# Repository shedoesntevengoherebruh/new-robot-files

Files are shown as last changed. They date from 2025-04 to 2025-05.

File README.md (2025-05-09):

This is the repository for the "BRONTE" (name subject to change) robotic chip-to-plate interface project.

Code and 3D model files are the joint work of Isabel B. Navarro and Gregory A. Datto.

>[!WARNING]
>
>_**This project (and its documentation) is still under development:**_ instructions are incomplete; the parts, object files, and code may change.

Thanks for stopping by the poster session!

P.S.— this is why it was really named BRONTE:

picture of BRONTE with scope

drawing of brontosaurus

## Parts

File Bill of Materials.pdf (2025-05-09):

## 1 Introduction

### 1.1 Bill of Materials

Designator | Manufacturer | Part # | Number | Cost/each | Total cost
| (Distributor)
Mechanical
Coupler | Uxcell | 1008917 | 1 (pack of 4) | $10.22 | $10.22
| (Harfington) | | (need 4)
Lead screw | McMaster-Carr | 99030A100 | 1 (3′
| | | length) | $46.42 | $46.42
Tapped shaft | McMaster-Carr | 6649K396 | 2 | $50.58 | $101.16
Ceramic-coated shaft | McMaster-Carr | 1031K72 | 2 | $16.52 | $33.04
3/8′′ linear bearing | AMPEC | SW06UU | 4 | $9.51 | $38.04
| (Bearings Direct)
3/8′′ ball bearing | AMPEC | R6-ZZ | 2 | $3.10 | $6.20
| (Bearings Direct)
1/4′′ shaft | McMaster-Carr | 1031K61 | 4 | $10.28 | $41.12
1/4′′ linear bearing | PBC Linear | IP04G | 4 | $17.04 | $68.16
M3 screw | McMaster-Carr | 92005A124 | 1 (pack of 100) | $5.79 | $5.79
| | | (need 16)
8-32 screw | McMaster-Carr | 91500A197 | 1(pack of 50) | $7.18 | $7.18
| | | (need 4)
Filament | ** | ** | **kgs | ≈ $20 | **
1/4′′ acrylic | AZM Displays | B07H9NQP8G | 1 (24′′x12′′) | $22.99 | $22.99
| (Amazon)
1/8′′ acrylic | McMaster-Carr | 8560K275 | 1 | $6.95 | $6.95
Electronics
Motor driver | Pololu | 2981 | 4 | $6.15 | $24.60
| (Digikey)
Permaproto boards* | Adafruit | 591 | 1 pack | $34.95 | $34.95
| (Microcenter)
NEMA-17 Motor with encoder | Stepper Online | 17HS15-1504-ME1K | 4 | $18.18 | $72.72
ESP32-s2 | Espressif | DevKitM-1-N4R2 | 1 | $8.00 | $8.00
| (Amazon)
Barrel jack adapter | Philmore | 48-1297 | 1 | $3.82 | $3.82
| (Microcenter)
Power supply | Alitove | ** | 1 | $37.99 | $37.99
| (Amazon)
Solder | ** | ** | ** | 1 | **
Pressure and Interface
Aluminum holder | ProtoLabs | N/A | N/A | ≈ $250 | ≈ $250
Headless Nut | IDEX | P-283 | 24 | $4.10 | $98.40
Ferrule | IDEX | P-200X | 1 *(pack of 10)* | $17.11 | $17.11
| | | (Need 6)
Luer Adapter | IDEX | P-625 | 8 | $5.21 | $41.68
Needle (Low Dead Space) | TSK | LDS-30009I | 1 (pack of 100) | $89.95 | $89.95
| (Air-Tite Products) | (TSK3009LDS) | (need 6)
Union | IDEX | *P-603 (white Delrin)* | 6 | $3.94 | $23.64
2-Port Kit | Elveflow | LVF-KPT-S-2 | 6 | $156.80 | $940.80
| (Darwin Microfluidics)
Pressure Regulator | Alicat Scientific | PCD-30PSIG-D-PCV30 | 6 | ≈$500 | ≈$3,000
| (eBay) | | | (Used)
DIN Jack | L-com | MD88FJF | 6 | $20.99 | $125.94

1

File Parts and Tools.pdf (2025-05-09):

# Methods Parts

## Tools

## Bill of Materials

See Bill of Materials PDF file.

## 3D printed pieces

This will be a table of the 3D printed parts, ideally with a picture or at least, color-coding of each one. I think the weight and time (when prepared as we did it), the number, the color (by our system), will be useful for people, along with the .stl or .obj filenames of each part, will be useful to include in the table.

Hammer/mallet (ideally, to help press-fit) 3D printer (with bed size at least X"xX"xX") set of small files
Allen key (Size X)
Phillips head screwdriver
Soldering station (with solder and fume extractor) hack saw (fresh blade ideal for cutting lead screw, etc.)

Tray (teal)
Carriage 1 (Yellow)
Carriage 1 endcaps (Yellow, 2×)
Carriage 2 (Magenta)
Carriage 2 endcap A and B (Magenta. Endcap A has the motor standoff.) "Big H" (white, 2×)
Lead screw nuts (black, 4×)

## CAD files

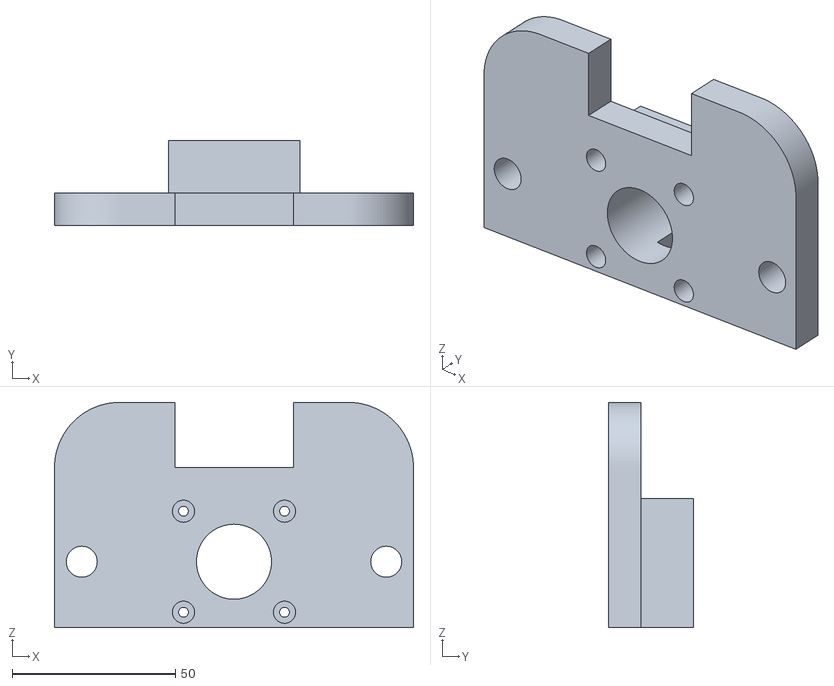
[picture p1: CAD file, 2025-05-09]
CAD files/Carriage 2 Endcap A.stl
110.1 x 26.0 x 69.1

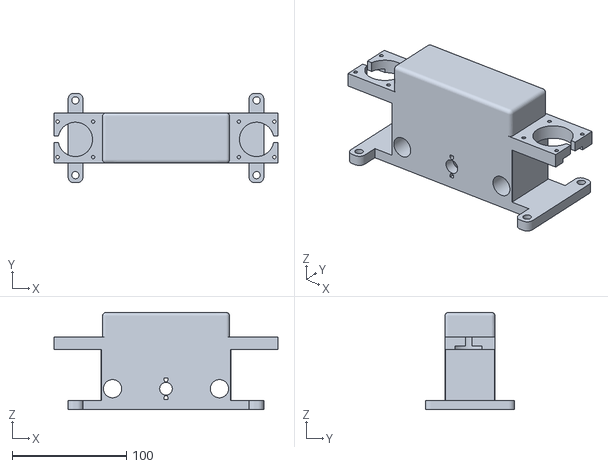
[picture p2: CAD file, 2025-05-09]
CAD files/Carriage 1.stl
195.7 x 78.1 x 84.8

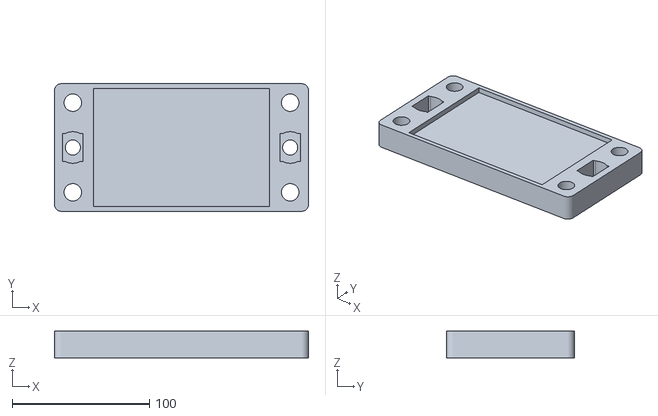
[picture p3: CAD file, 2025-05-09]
CAD files/Tray.stl
185.0 x 93.0 x 19.6

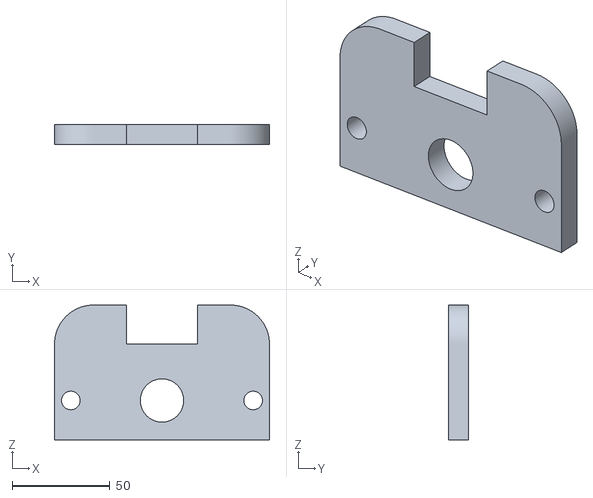
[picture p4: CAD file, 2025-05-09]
CAD files/Carriage 2 Endcap B.stl
110.1 x 10.0 x 69.1

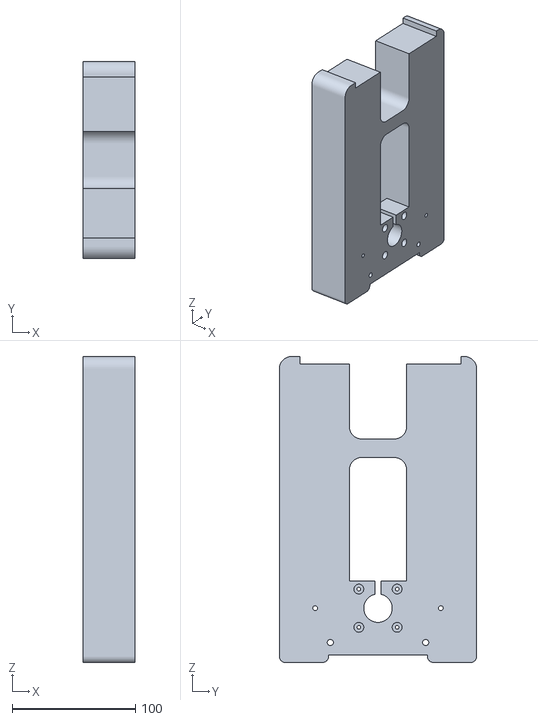
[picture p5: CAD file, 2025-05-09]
CAD files/BIG H.stl
42.0 x 160.0 x 248.0

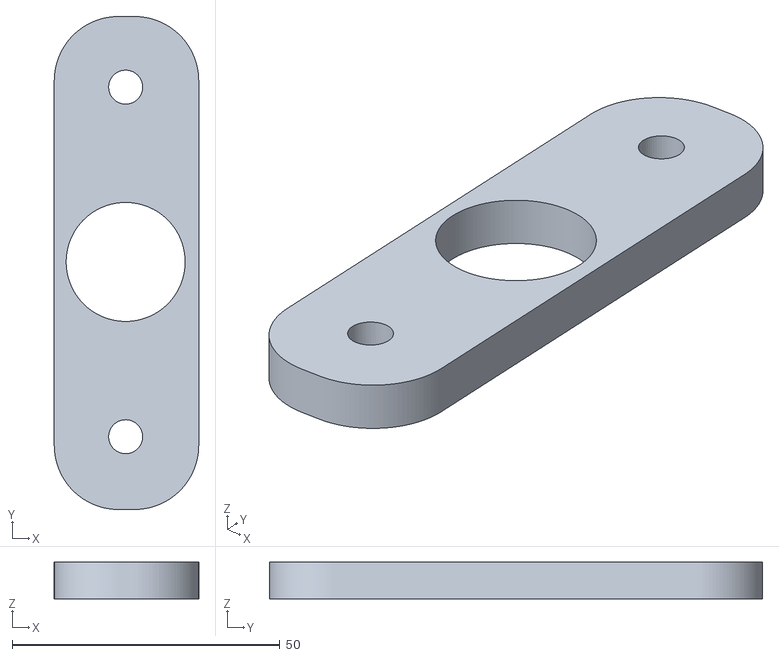
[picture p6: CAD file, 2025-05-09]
CAD files/Carriage 1 endcaps.stl
27.0 x 92.1 x 6.90

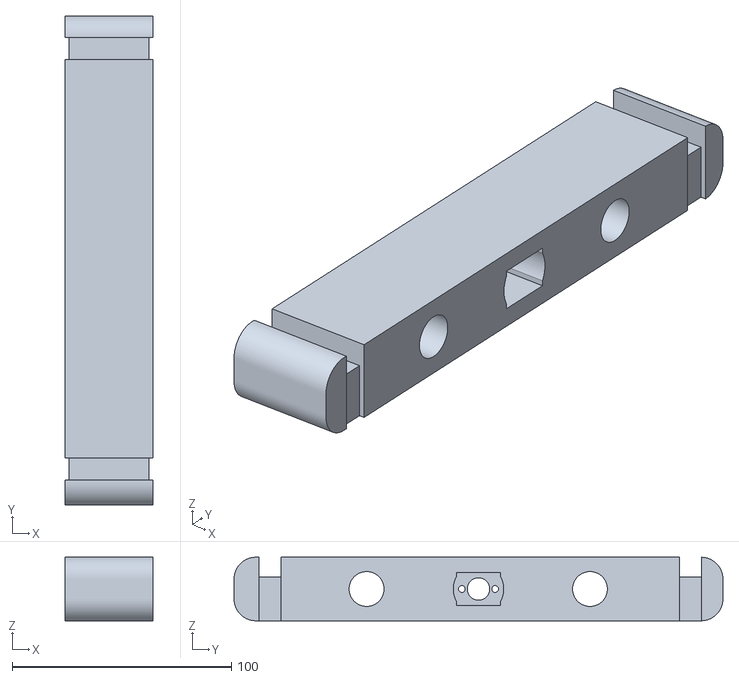
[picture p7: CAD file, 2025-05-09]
CAD files/Carriage 2.stl
40.3 x 222.8 x 29.0

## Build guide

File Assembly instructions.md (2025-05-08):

# Mechanical

> [!NOTE]
> Probably need to rewrite this in the past tense instead of as directive instructions. However, the tips really make the most sense as instructions. idk. it's a draft.
> -Izzy

> [!CAUTION]
> If using vise grips to wiggle any press-fit shafts into/through holes, ONLY APPLY THEM at the END of the shaft. They WILL damage the ceramic coating, which will add more friction if that mark is in the middle of the shaft.

## Assembly
### 1. Print all pieces. 
Then, remove supports. Conservatively file down any obvious irregularities in circular holes which were printed upright (Carriage 1).
(If you're in a hurry, print Tray, Carriage+Endcaps 1, and ¾ (or all 4) lead screw nuts first, as you'll assemble them first, then Carriage+Endcaps 2 with the final lead screw nut, then the Big Hs, either one at a time, or together, remembering that you will certainly need to replace the filament spool if using a standard 1kg spool.)

### 2. Assemble "Tray".
- Press-fit 1/4" linear bearings into the 4 corners of this tray until flush. 
- Press-fit a black lead screw nut into the shaped hole in each end, filing any imprecisions conservatively as needed.

### 3. Assemble Carriage 1.
- Press-fit ⅜" linear bearings in the appropriate holes (bottom left and right) of Carriage 1. You may wish to arrange Carriage 1 on its side, diagonally, around the corner of a table, for support.
- Press-fit a black lead screw nut into the center hole of Carriage 1, filing any imprecisions conservatively as needed.


### 4. Attach Tray to Carriage 1.
- **Cut two [^2]3" lengths from the lead screw stock.**
- Slide motors into place on either end, with the cables facing to the same side (either left or right), then secure with four M3 screws.
	

- Grasp the shaft of one motor and turn its flat side to face the gap at the end of the mounting area. Repeat on the other side.
- Slide a coupler over the motor shaft (with the narrow end facing the motor) and align one vertical set of set screws with the flat side of the shaft. Holding the coupler up so that the lower screw will hit the flattened length, tighten the lower set screw with the **[^1]allen key**. ~~Ideally, the end of the motor shaft will be in the center of the coupler, so that the lead screw can be held securely within the coupler as well~~. 

==The top of the coupler MUST be below the top of Carriage 1 for calibration purposes. Therefore==:

- Partially tighten the lower set screw (of the pair aligned with the flat side of the motor shaft). Allow the coupler to slide down the shaft until the set screw hits ==the end of the flattened area== (the lowest the coupler can sit on the motor shaft). This will ensure that the top of the coupler sits below the top surface of Carriage 1, which is necessary for calibration purposes.
- 
- Turn the coupler and shaft so that you can tighten the second lower screw in the same manner. Repeat on the other motor.
	

- Pull the motor cables towards the center so that they are not blocking the 1/4" holes in the bottom of Carriage 1. Fit one 1/4" shaft into one of the small holes in the arms at the bottom, gently tapping into place as needed on a flat surface. Repeat for the other three holes.
	

- Slide 1/4" bearings of Tray over the 1/4" shafts until it sits on the top surface of Carriage 1.
	

- Drop one of the [^2]3" lengths of lead screw through one of the lead screw nut of the tray and into the coupler. Tighten each of the upper set screws of the coupler to hold the lead screw in place. Repeat on the other side. (The two sides are now naturally aligned/in the same vertical position because they were installed while the tray was resting on the top horizontal surface of Carriage 1.) (Solid coupler was chosen over flexible couplers, as this cartesian system requires alignment. I didn't know anything about anything when I started and tried it with flexible couplers. those allowed the screws to be installed misaligned, leading to seizing/jamming issues. Ideally, these would be ⅜" to 5mm couplers. The 10mm coupler allows for ~500um misalignment, but this has not caused any perceptible issues in operation yet, perhaps due in part to the ⅜" rotary bearing on the other side.)

> [!NOTE]
> Hahahaha idk why it's sooooo sticky as if it's misaligned? maybe this will resolve when I put the little lid on (help straighten it out??) end me lmao
> I did have to sand basically everything... ideally I would adjust the prints to not need this but idk
> 
> Ok, what I did to get it fairly loose was to loosen the screws holding the lead screw in place, and re-set them after rotating the coupler somewhat. Also, I did not tighten the first screw ALL THE WAY, but just enough to feel resistance, then did the second one, then came back— 'IKEA-style'— to avoid pushing the lead screw in one direction or another (by that 500um or whatever.) This actually had a big impact and needs to go into the instructions later

- Press fit a ⅜" rotary bearing in the center hole of each of the Carriage 1 endcaps.
	

- Align the remaining holes with a pair of the installed 1/4" shafts, and gently tap into place, inverting onto a flat surface if needed, to press-fit the endcaps on, capturing the tray on Carriage 1.
	

### 5. Assemble Carriage 2.

> [!note]
> - not sure if single M3 screw length is long enough for the Carriage 2 built-in standoff.
> - wires vs. cables talking about those running from the motors
> - also, I would maybe shorten the NEMA-17 stepper motor with encoder to just motor (for obvious reasons... but I don't want to make the table any wider!)

- Press-fit the two ceramic shafts into their respective holes in Carriage 2 Endcap A, such that the shafts extend from the flat face, and are flush with the face on the opposite side of the hole. (This can be achieved by holding the endcap against the edge of a table, with the flat face upwards, the square protrusion resting against the edge of the table, and the hole intended for the shafts over the table surface.)
	

- Slide a coupler (narrow side of hole closest to the motor— like, the side designed for motor shafts should be on the motor shaft, obviously!), onto the shaft of one of the remaining motors. Align one of the vertical sets of set screws with the flat side of the shaft, then tighten both of the lower [^4] set screws to affix[^3] the coupler to the motor shaft.

> [!NOTE]
> if you put it all the way down, then you can't adjust the upper screws after attaching the motor to Carriage 2, making it harder to put the lead screw in. I guess I would recommend a different technique than for the other two motors.
> 

- Align this motor with the square protrusion of Carriage 2 Endcap A, so that the shaft is centered in the circular hole within that square, the front face of the motor is flush with the square protrusion, and the side of the motor with the cables is facing towards the large notch/concave side of Endcap A (which will face the bottom/downwards).
- Attach motor to (Carriage 2) Endcap A in this position with four M3 screws.
- Press fit a ⅜" rotary bearing in the center hole of Carriage 2 Endcap B. 
- Carefully sand any obvious irregularities in the ⅜" holes in Carriage 2 Endcap B to prepare it for press-fitting.
- Slide the ⅜" linear bearings of Carriage 1 over the ⅜" ceramic shafts of Endcap A, with the top of the tray facing opposite the large notch in Carriage 2 endcap A (large notch will point towards the table, tray needs to point upwards to carry the collection plates.)
- Press fit/slide Carriage 2 Endcap B (with profile matching/oriented the same as Endcap A) onto the end of the ceramic shafts, capturing Carriage 1. This can be accomplished by tapping the area around the ⅜" shaft/hole with a hammer, while supporting the opposite end of the shaft (attached to endcap A) with the edge of a table. Continue tapping and checking against Carriage 2, until Endcap B is far enough along the ceramic shafts so that Endcap A and B can slide into their cutouts on Carriage 2. 

> [!WARNING]
> This step is the worst. Pretty hard to tell if there's actually a good way to do this or not. sorry.
> 



> [!NOTE]
> Couldn't they just affix the bottom part of the coupler before attaching the motor to the endcap? I think that would be easier lol.
> 
> 

- Press-fit ⅜" linear bearings into the circular holes in Carriage 2. Press-fit black 3D-printed lead screw nut into its slot.
	

> [!NOTE]
> I usually do it with the flat side facing the bottom of the hole, but it literally shouldn't matter either way.
> 

- ==Press-fit/snap/lock in place Endcap A and B (with the attached motor) to Carriage 2 via their corresponding slots==. ==Not sure if direction matters, it shouldn't== 
	

> [!NOTE]
>  which side they put the motor on matters for the XY motors because of the direction it turns. so we actually **do** want to recommend one of the two sides, otherwise they would have to adjust the code directionality.
> 

- Cut 9-10" segment from lead screw stock. 
- Thread this 9" section of lead screw through the ⅜" rotary bearing of Endcap B, through the black lead screw nut in Carriage 2, and into the Coupler on the motor attached to Endcap A.
- Tighten the two set screws in that Coupler, first part-way, then fully, to affix (==different word choice==) the lead screw in the coupler. 

> [!NOTE]
> If you don't do this, you run the risk of misaligning the lead screw in the coupler by pushing it all the way to one side. 
> 

> [!NOTE]
> Ceramic-coated shaft is a bad name for Carriage 2 shafts because I also selected ceramic-coated for the 1/4" shafts
> Also, 9-10" is based on it needing to be about the same length as the ceramic shafts used in Carriage 2. 9" is likely fine, especially since the shafts are longer than the actual separation of the two endcaps of Carriage 2.

### 6. Final ()

[^1]: What size allen key for the coupler set screws?

[^2]: What length for these jawns? It depends on the length we end up with for the overall height.... and that is still somewhat up in the air with Greg about being able to switch from tall to short plates. I think an extra inch will work but we still have to confirm by taking measurements.

[^3]: use different word lol

[^4]: lower meaning closer to the motor, lower on the shaft... does it need to be clearer than this? 

# Electronics

(to be continued)

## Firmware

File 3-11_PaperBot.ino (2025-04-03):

//Libraries needed
#include <Wire.h>
#include <HardwareSerial.h>
//AccelStepper.h was used previously, but has been replaced with a custom library outlined below.

//encoder stuff below
//encoders have two signals, A+B, which are square waves,
//having just one signal allows for tracking motion and position, but not direction—
//with both, one can extrapolate direction from which 

#define ENCODER_A1 7  // Must be an interrupt-capable pin (21) attached to Z motor 1
#define ENCODER_B1 8  // Must be an interrupt-capable pin (30) attached to Z motor 1

volatile long encoderPosition1 = 0;
volatile long global_target_encoderPosition1 = 0;
volatile int lastEncoded1 = 0;


#define ENCODER_A2 3  // Must be an interrupt-capable pin 2, attached to Z motor 2
#define ENCODER_B2 4  // Must be an interrupt-capable pin 3, attached to Z motor 2

volatile long encoderPosition2 = 0;
volatile long global_target_encoderPosition2 = 0;
volatile int lastEncoded2 = 0;

#define ENCODER_Ax 5  // Must be an interrupt-capable pin, attached to X-axis motor
#define ENCODER_Bx 6  // Must be an interrupt-capable pin, attached to X-axis motor

long encoderPositionx = 0;
long global_target_encoderPositionx = 0;
int lastEncodedx = 0;

#define ENCODER_Ay 1  // Must be an interrupt-capable pin, attached to Y-axis motor
#define ENCODER_By 2  // Must be an interrupt-capable pin, attached to Y-axis motor

volatile long encoderPositiony = 0;
volatile long global_target_encoderPositiony = 0;
volatile int lastEncodedy = 0;

//end encoder stuff

//pressure regulator settings below

int ArdBaud = 19200;   // Baud rate for the serial monitor [on the Arduino]
int AlctBaud = 19200;  // Baud rate on the Alicat (see RS-232 settings); default is 19200

int TxPin = 49;  // Arduino Tx pin, connected to the Alicat Rx RS-232 pin (pin 3 on the 8 pin mini-DIN)
int RxPin = 50;  // Arduino Rx pin, connected to the Alicat Tx RS-232 pin (pin 5 on the 8 pin mini-DIN)

const int NUMBER_OF_FORMULATIONS = 4;

//timing for flushing and collecting

int flush_time = 20000; //time to flush lines, ms
int collect_time = 15000;//time to collect, ms

// Array of strings to store pressure values for each formulation
char arr[NUMBER_OF_FORMULATIONS][6][10] = { //the 10 on this array is for 10 bits of each number's string.
  { "16", "24", "24", "24", "36", "36" },
  { "20", "20", "24", "30", "30", "36" },
  { "24", "16", "24", "36", "24", "36" },
  { "28", "12", "24", "42", "18", "36" },
};


HardwareSerial mySerial(2); //defines that we are using TX1 and RX1 UART pins of ESP32 chip, which are pins 17+18
#define RXD1 18 //RXD pin used on ESP32
#define TXD1 17 //TXD pin used on ESP32

char PressureE1[10]; //all the packets sent to pressure regs are 10 characters long (length of ten bytes).
char PressureE2[10];
char PressureE3[10];
char PressureA1[10];
char PressureA2[10];
char PressureA3[10];

const int reg_array_size = 30;//for an array that keeps the 30 most recent pressure values

int E1_reg_array[reg_array_size] = { 0 };
int E2_reg_array[reg_array_size] = { 0 };
int E3_reg_array[reg_array_size] = { 0 };
int A1_reg_array[reg_array_size] = { 0 };
int A2_reg_array[reg_array_size] = { 0 };
int A3_reg_array[reg_array_size] = { 0 };

int formulation_counter = 0; //iterator variable
int pressureFormulation = 0; //iterator variable

// int E1 = 5; //assigning pins for each regulator.
// int E2 = 6;
// int E3 = 7;
// int pin_A1 = 8;
// int pin_A2 = 12;
// int pin_A3 = 13;

int E1_reg_pin = A15; //assigning pins for each regulator
int E2_reg_pin = A13;
int E3_reg_pin = A14;
int A1_reg_pin = A12;
int A2_reg_pin = A11;
int A3_reg_pin = A10;

int delta_smooth = 5; //limit on the acceptable smoothness of PID signal
int delta_abs = 10; //limit on pressure accuracy
bool kill_switch = false; //kill switch/button variable.

bool equilibrate = true; //state variable

int R_index = 0; // the index in the regulator array, the current pressure
int counter = 0; // iterator variable for the position in the regulator array (I think)

//end pressure regulator settings

// Constants and Configurations (global variables for robotic motion)
int z_top = 1000; //in steps, from the bottom position. equivalent to 5".
int Z_HOME = 4000; //comfortable height where needles are retracted and won't brush the plate, in terms of encoder steps.
float inch_rot = 1; // the number of lateral inches moved per rotation is 1. yes, inches.
float act_rot = 200; //the number of actuations per rotation is 800 
float enc_rot = 4000; // the number of encoder counts per rotation is 4000
int delaymotor = 500; // the number of microseconds used for delays between steps.
bool moveFlag = false;

//BASED ON THE PLATE USED: MAY CHANGE
const int STEPS_TO_BOTTOM_Z = 11195;//in steps; position where needles are fully within the wells. referenced from top so take off z-home for all other movements was +425
const int center_x_1 = 3550; //X distance from starting point to X center of first well (upper left) in encoder steps
const int center_y_1=7100; // Y distance from starting point to Y center of first well in encoder steps.
const int Y_STEPS_PER_POSITION = 5669; //distance between y positions, in terms of steps. Will change if plate is changed.
const int X_STEPS_PER_POSITION = 2835; //distance between X positions, in terms of steps. Will change is plate is changed.

//pins
const int DIR_PIN_z1 = 41;
const int STEP_PIN_z1 = 42;
const int DIR_PIN_z2 = 37; //46
const int STEP_PIN_z2 = 38; //47
const int DIR_PIN_y = 35;
const int STEP_PIN_y = 36;
const int DIR_PIN_x = 39;
const int STEP_PIN_x = 40;


const int Calibration_BUTTON = 12; //pin for button

bool comm_value = true;


bool first_round_flag = true;

// Functionality variables
bool verticalStepperDir = false; //flip to change directionality of Z motor
bool finishedFlag = false; //used to stop the void loop()

//New functions defined

// updateEncoder functions track the position of each motor
void updateEncoder1() {
    int A_1 = digitalRead(ENCODER_A1);
    int B_1 = digitalRead(ENCODER_B1);
    int encoded1 = (A_1 << 1) | B_1;
    int sum1 = (lastEncoded1 << 2) | encoded1;

    if (sum1 == 0b0001 || sum1 == 0b0111 || sum1 == 0b1110 || sum1 == 0b1000) {
        encoderPosition1++;
    } else if (sum1 == 0b0010 || sum1 == 0b1101 || sum1 == 0b1011 || sum1 == 0b0100) {
        encoderPosition1--;
    }
    lastEncoded1 = encoded1;
}

void updateEncoder2() {
    int A_2 = digitalRead(ENCODER_A2);
    int B_2 = digitalRead(ENCODER_B2);
    int encoded2 = (A_2 << 1) | B_2;
    int sum2 = (lastEncoded2 << 2) | encoded2;

    if (sum2 == 0b0001 || sum2 == 0b0111 || sum2 == 0b1110 || sum2 == 0b1000) {
        encoderPosition2++;
    } else if (sum2 == 0b0010 || sum2 == 0b1101 || sum2 == 0b1011 || sum2 == 0b0100) {
        encoderPosition2--;
    }
    lastEncoded2 = encoded2;
}

void updateEncoderx(){

  int A_x = digitalRead(ENCODER_Ax);
  int B_x = digitalRead(ENCODER_Bx);
  int encodedx = (A_x << 1) | B_x;
  int sumx = (lastEncodedx << 2) | encodedx;
  if (sumx == 0b0001 || sumx == 0b0111 || sumx == 0b1110 || sumx == 0b1000) {
      encoderPositionx++;
  } else if (sumx == 0b0010 || sumx == 0b1101 || sumx == 0b1011 || sumx == 0b0100) {
      encoderPositionx--;
  }
  lastEncodedx = encodedx;
}

void updateEncodery(){
  int A_y = digitalRead(ENCODER_Ay);
  int B_y = digitalRead(ENCODER_By);
  int encodedy = (A_y << 1) | B_y;
  int sumy = (lastEncodedy << 2) | encodedy;
  if (sumy == 0b0001 || sumy == 0b0111 || sumy == 0b1110 || sumy == 0b1000) {
    encoderPositiony++;
  } else if (sumy == 0b0010 || sumy == 0b1101 || sumy == 0b1011 || sumy == 0b0100) {
    encoderPositiony--;
  }
  lastEncodedy = encodedy;
}

//move [] stepper(s) functions written to replace accelstepper library. 

void move_x_stepper(long number_of_encoder_counts, int dir){
  int step_type = 1;
  if (dir == 0){
    global_target_encoderPositionx = global_target_encoderPositionx - number_of_encoder_counts;
    while (abs(global_target_encoderPositionx - encoderPositionx)>5){
      int fudge_steps = (int)((((float)(encoderPositionx-global_target_encoderPositionx))/enc_rot)*act_rot);
      if (fudge_steps < 0){
        digitalWrite(DIR_PIN_x,LOW);
        for (int x=0;x<abs(fudge_steps);x++){
          digitalWrite(STEP_PIN_x,HIGH);
          delayMicroseconds(delaymotor);
          digitalWrite(STEP_PIN_x,LOW);
          delayMicroseconds(delaymotor);
        }
      }
      else{
        digitalWrite(DIR_PIN_x,HIGH);
        for (int x=0;x<abs(fudge_steps);x++){
          digitalWrite(STEP_PIN_x,HIGH);
          delayMicroseconds(delaymotor);
          digitalWrite(STEP_PIN_x,LOW);
          delayMicroseconds(delaymotor);
        }
      }
    }
  }
  else{
    global_target_encoderPositionx = global_target_encoderPositionx + number_of_encoder_counts;
    while (abs(global_target_encoderPositionx- encoderPositionx)>5){
      int fudge_steps = (int)((((float)(encoderPositionx-global_target_encoderPositionx))/enc_rot)*act_rot);

      if (fudge_steps < 0){
        digitalWrite(DIR_PIN_x,LOW);
        for (int x=0;x<abs(fudge_steps);x++){
          digitalWrite(STEP_PIN_x,HIGH);
          delayMicroseconds(delaymotor);
          digitalWrite(STEP_PIN_x,LOW);
          delayMicroseconds(delaymotor);
        }
      }
      else{
        digitalWrite(DIR_PIN_x,HIGH);
        for (int x=0;x<abs(fudge_steps);x++){
          digitalWrite(STEP_PIN_x,HIGH);
          delayMicroseconds(delaymotor);
          digitalWrite(STEP_PIN_x,LOW);
          delayMicroseconds(delaymotor);
        }
      }
    }
  }
}


void move_y_stepper(int number_of_encoder_counts, int dir){
  int step_type = 1;
  if (dir == 0){
    global_target_encoderPositiony = global_target_encoderPositiony - number_of_encoder_counts;
    while (abs(global_target_encoderPositiony - encoderPositiony)>5){
      int fudge_steps = (int)((((float)(encoderPositiony-global_target_encoderPositiony))/enc_rot)*act_rot);
      if (fudge_steps < 0){
        digitalWrite(DIR_PIN_y,LOW);
        for (int y=0;y<abs(fudge_steps);y++){
          digitalWrite(STEP_PIN_y,HIGH);
          delayMicroseconds(delaymotor);
          digitalWrite(STEP_PIN_y,LOW);
          delayMicroseconds(delaymotor);
        }
      }
      else{
        digitalWrite(DIR_PIN_y,HIGH);
        for (int y=0;y<abs(fudge_steps);y++){
          digitalWrite(STEP_PIN_y,HIGH);
          delayMicroseconds(delaymotor);
          digitalWrite(STEP_PIN_y,LOW);
          delayMicroseconds(delaymotor);
        }
      }
    }
  }
  else{
    global_target_encoderPositiony = global_target_encoderPositiony + number_of_encoder_counts;
    while (abs(global_target_encoderPositiony- encoderPositiony)>5){
      int fudge_steps = (int)((((float)(encoderPositiony-global_target_encoderPositiony))/enc_rot)*act_rot);
      if (fudge_steps < 0){
        digitalWrite(DIR_PIN_y,LOW);
        for (int y=0;y<abs(fudge_steps);y++){
          digitalWrite(STEP_PIN_y,HIGH);
          delayMicroseconds(delaymotor);
          digitalWrite(STEP_PIN_y,LOW);
          delayMicroseconds(delaymotor);
        }
      }
      else{
        digitalWrite(DIR_PIN_y,HIGH);
        for (int y=0;y<abs(fudge_steps);y++){
          digitalWrite(STEP_PIN_y,HIGH);
          delayMicroseconds(delaymotor);
          digitalWrite(STEP_PIN_y,LOW);
          delayMicroseconds(delaymotor);
        }
      }
    }
  }
}
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

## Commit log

2025-04-03 Create 3-11_PaperBot.ino
    copied the original code that was working to put holes in 5 times. 4/3/2025
2025-05-07 first version of assembly instructions.
    First draft of mechanical assembly instructions. Does not include electrical designs yet.
2025-05-07 Update Assembly instructions.md
    fixed images not linked
2025-05-07 Update Assembly instructions.md
    fixed images not correctly linked
2025-05-08 adding video
    first videos. not attached to regulators.
2025-05-09 upload .stl files of 3D printed parts
    as of May 9th, 2025
    [BIG H.stl, Carriage 1 endcaps.stl, Carriage 1.stl, Carriage 2 Endcap A.stl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]
2025-05-09 necessary materials
    first upload of bill of materials, parts, and tools lists.
